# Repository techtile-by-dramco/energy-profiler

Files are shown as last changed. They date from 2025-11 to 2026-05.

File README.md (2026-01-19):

# 🔍 Energy Profiler 🔍

This repository contains 
- the **hardware** files (including the controller board)
- the **firmware** running on the controller board
- the **publisher script** (which receives information from the controller board over a USB connection)
- an example **subscriber script**

### Updates ToDo 📝
- ???

### Test Energy Profiler script
1. Test `/publisher-script/main_last.py`
2. Run services
	1. Copy service files to systemd:
	```
	sudo cp ~/energy-profiler/ep.service /lib/systemd/system/
 	```
 	2. Enable and start services
  	```
   	sudo systemctl enable ep.service
   	sudo systemctl start ep.service
  	```   
### Update energy profiler service
	
```
sudo cp ~/energy-profiler/ep.service /etc/systemd/system/
sudo systemctl daemon-reload
sudo systemctl restart ep.service
```

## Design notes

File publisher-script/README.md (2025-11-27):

### Publischer script

Executed on the windows server

NRF52 development board is used to receive BLE advertisement packets and communicates/send them to the windows computer via a serial port.

Finally the energy profiler data from serial port is published via ZMQ on port 5556

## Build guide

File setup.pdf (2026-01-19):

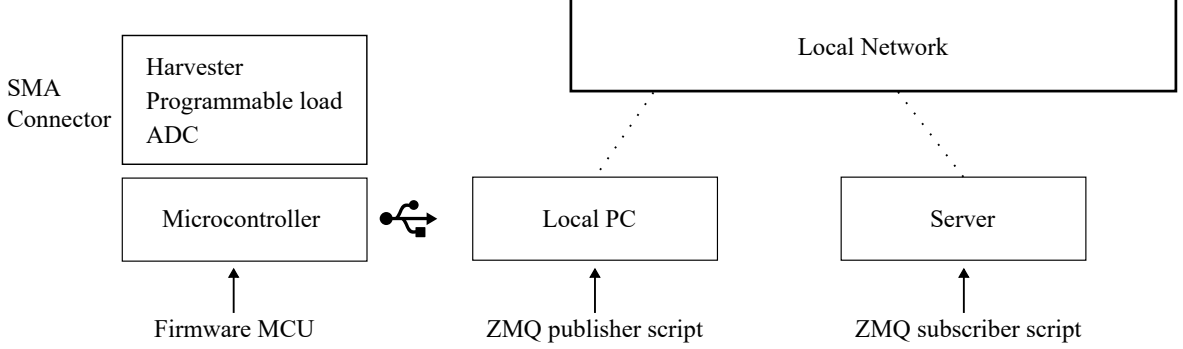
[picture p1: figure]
Microcontroller; Firmware MCU; Local PC; Local Network; Server; Programmable load; Harvester; ADC; SMA Connector; ZMQ publisher script; ZMQ subscriber script

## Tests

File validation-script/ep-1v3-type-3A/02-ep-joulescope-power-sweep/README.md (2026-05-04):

## JouleScope Measuements

Votage of the power supply was 2V in following measurement.
Power supply was connected to the joulescope and the energy profiler.
The current passes through the JouleScope.

"Joulescope switches shunt resistors in approximately 1 μs on over-range to keep your target device running correctly. It maintains a maximum burden voltage of 20 mV across the shunt resistor, for any current up to 2 A. Joulescope is electrically isolated to avoid any grounding and ground loop concerns." [See here](https://www.joulescope.com/blogs/blog/how-to-measure-current).

### Processing 1: Results

Power consumed in the EP calculated via energy profiler itself.

<!-- ![](https://github.com/techtile-by-dramco/energy-profiler/blob/main/validation-script/ep-1v3/02-ep-joulescope-power-sweep/js_vs_ep_P1.png)
![](https://github.com/techtile-by-dramco/energy-profiler/blob/main/validation-script/ep-1v3/02-ep-joulescope-power-sweep/js_vs_ep_delta_P1.png)
![](https://github.com/techtile-by-dramco/energy-profiler/blob/main/validation-script/ep-1v3/02-ep-joulescope-power-sweep/js_vs_ep_error_P1.png)
![](https://github.com/techtile-by-dramco/energy-profiler/blob/main/validation-script/ep-1v3/02-ep-joulescope-power-sweep/js_vs_ep_error_log_P1.png)
![](https://github.com/techtile-by-dramco/energy-profiler/blob/main/validation-script/ep-1v3/02-ep-joulescope-power-sweep/js_vs_pot_val_P1.png) -->

### Processing 2: Results

Power consumed in the EP NOT calculated via energy profiler itself.

Due to energy loss over the internal JouleScope shunt resistor, the voltage measured by the energy profiler drops.
Therefore the EP power is calculated via JouleScope voltage in the following graphs.

<!-- ![](https://github.com/techtile-by-dramco/energy-profiler/blob/main/validation-script/ep-1v3/02-ep-joulescope-power-sweep/js_vs_ep_P2.png)
![](https://github.com/techtile-by-dramco/energy-profiler/blob/main/validation-script/ep-1v3/02-ep-joulescope-power-sweep/js_vs_ep_delta_P2.png)
![](https://github.com/techtile-by-dramco/energy-profiler/blob/main/validation-script/ep-1v3/02-ep-joulescope-power-sweep/js_vs_ep_error_P2.png)
![](https://github.com/techtile-by-dramco/energy-profiler/blob/main/validation-script/ep-1v3/02-ep-joulescope-power-sweep/js_vs_ep_error_log_P2.png)
![](https://github.com/techtile-by-dramco/energy-profiler/blob/main/validation-script/ep-1v3/02-ep-joulescope-power-sweep/js_vs_pot_val_P2.png) -->

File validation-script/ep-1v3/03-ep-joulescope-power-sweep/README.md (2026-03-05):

## JouleScope Measuements

Voltage with the JouleScope is measured after the JouleScope shunt resistor

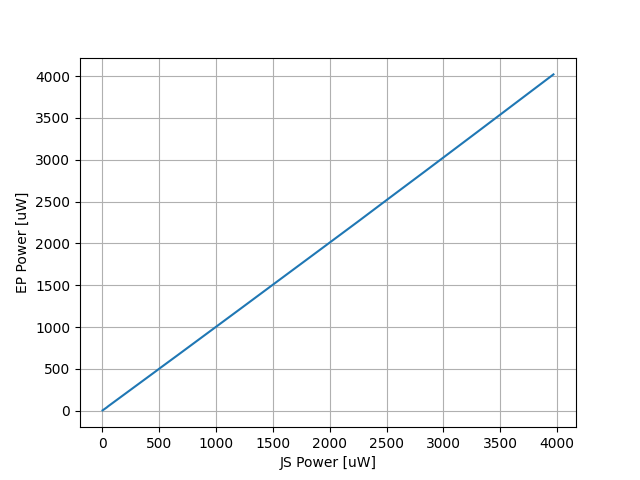
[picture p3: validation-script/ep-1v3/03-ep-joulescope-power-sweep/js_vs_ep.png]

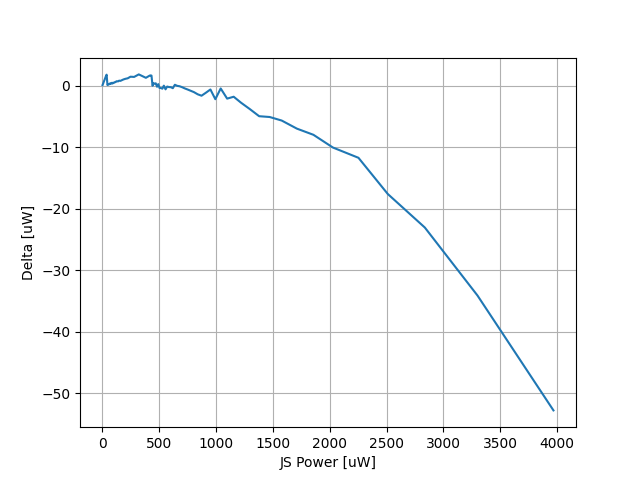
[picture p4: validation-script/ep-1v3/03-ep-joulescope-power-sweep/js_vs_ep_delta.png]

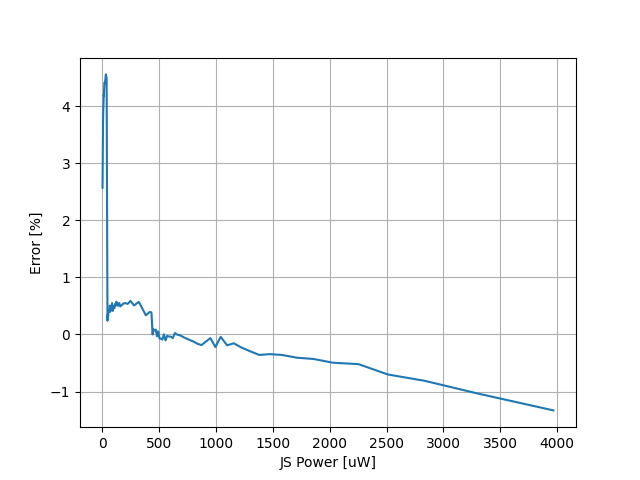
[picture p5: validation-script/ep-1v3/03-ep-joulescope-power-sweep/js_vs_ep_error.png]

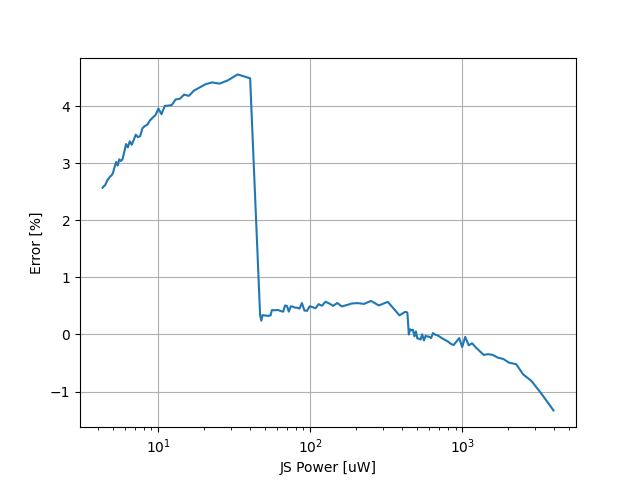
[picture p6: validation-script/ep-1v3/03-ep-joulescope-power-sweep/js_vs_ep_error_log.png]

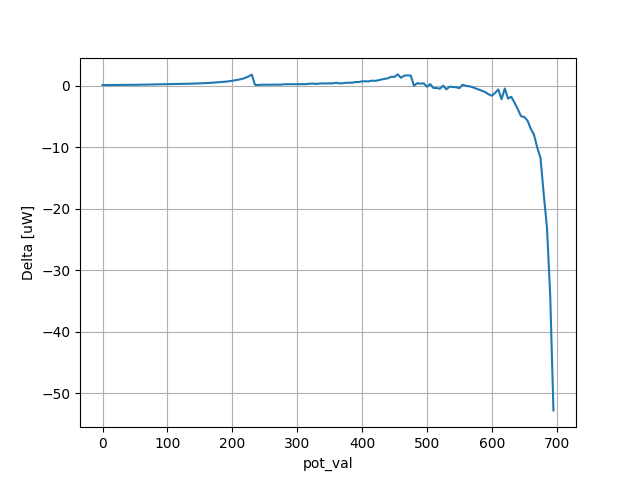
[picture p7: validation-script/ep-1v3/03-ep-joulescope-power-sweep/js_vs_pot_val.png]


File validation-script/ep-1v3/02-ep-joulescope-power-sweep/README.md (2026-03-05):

## JouleScope Measuements

Votage of the power supply was 2V in following measurement.
Power supply was connected to the joulescope and the energy profiler.
The current passes through the JouleScope.

"Joulescope switches shunt resistors in approximately 1 μs on over-range to keep your target device running correctly. It maintains a maximum burden voltage of 20 mV across the shunt resistor, for any current up to 2 A. Joulescope is electrically isolated to avoid any grounding and ground loop concerns." [See here](https://www.joulescope.com/blogs/blog/how-to-measure-current).

### Processing 1: Results

Power consumed in the EP calculated via energy profiler itself.

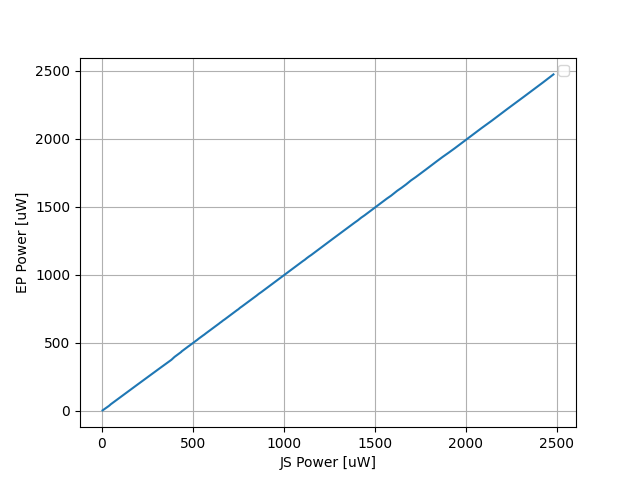
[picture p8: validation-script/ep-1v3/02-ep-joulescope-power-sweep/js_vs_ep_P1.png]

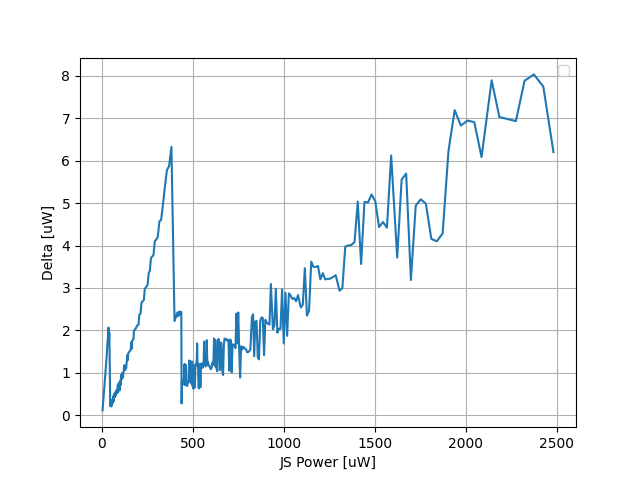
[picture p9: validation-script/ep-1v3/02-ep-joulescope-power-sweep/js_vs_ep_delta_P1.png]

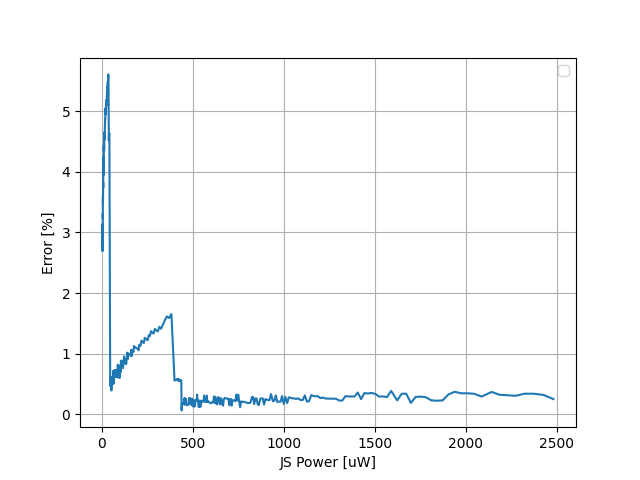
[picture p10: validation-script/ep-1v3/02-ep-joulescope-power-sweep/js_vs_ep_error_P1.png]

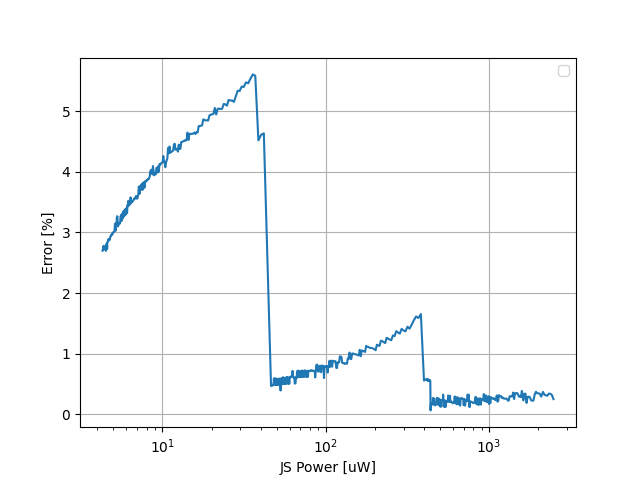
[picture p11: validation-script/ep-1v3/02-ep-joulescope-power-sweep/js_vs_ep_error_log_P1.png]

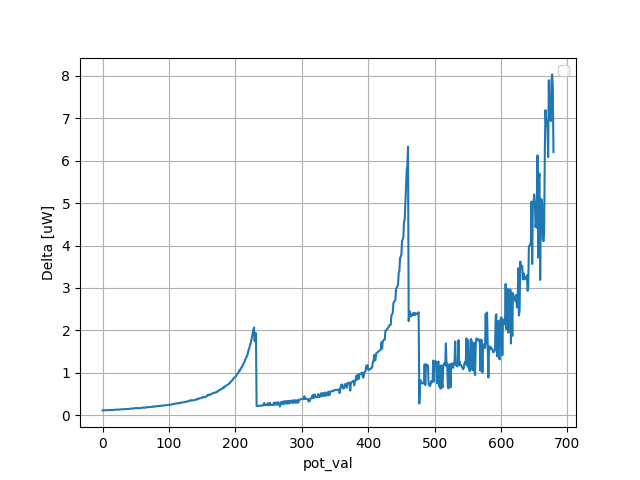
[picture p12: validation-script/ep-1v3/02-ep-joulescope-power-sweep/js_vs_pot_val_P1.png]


### Processing 2: Results

Power consumed in the EP NOT calculated via energy profiler itself.

Due to energy loss over the internal JouleScope shunt resistor, the voltage measured by the energy profiler drops.
Therefore the EP power is calculated via JouleScope voltage in the following graphs.







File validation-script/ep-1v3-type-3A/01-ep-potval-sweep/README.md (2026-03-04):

## Potentiometer calibration

The HAMEG HM8112-3 was connected to the input of the energy profiler. The AUTO_RESISTANCE_TUNE parameter was disabled in the firmware. A sweep was performed over all potentiometer values to calibrate the energy profiler using a lookup table implemented in the firmware. The results of the calibrated energy profiler are presented below.



### Sweep


### Error (absolute)


### Error (percentage)


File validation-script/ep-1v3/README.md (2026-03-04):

## Validation with Measuements of Energy Profiler Version 1.3

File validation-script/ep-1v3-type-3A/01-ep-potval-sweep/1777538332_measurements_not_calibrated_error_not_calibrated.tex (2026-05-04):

% This file was created with matplot2tikz v0.5.4.
\begin{tikzpicture}

\definecolor{darkgray176}{RGB}{176,176,176}
\definecolor{steelblue31119180}{RGB}{31,119,180}

\begin{axis}[
tick align=outside,
tick pos=left,
x grid style={darkgray176},
xlabel={Digital potentiometer Index},
xmajorgrids,
xmin=-35.9, xmax=753.9,
xtick style={color=black},
y grid style={darkgray176},
ylabel={Resistance Error},
ymajorgrids,
ymin=-8861.3, ymax=40359.3,
ytick style={color=black}
]
\addplot [semithick, steelblue31119180]
table {%
0 38122
1 37749
2 37259
3 36760
4 36537
5 36312
6 35439
7 34929
8 34951
9 34097
10 33705
11 33231
12 32777
13 32348
14 31900
15 30555
16 29917
17 30210
18 29782
19 29692
20 29167
21 29634
22 31906
23 28051
24 27577
25 27153
26 26771
27 26415
28 25956
29 25496
30 25150
31 24737
32 24340
33 24346
34 23442
35 23142
36 22827
37 22362
38 22057
39 21357
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
};
\end{axis}

\end{tikzpicture}

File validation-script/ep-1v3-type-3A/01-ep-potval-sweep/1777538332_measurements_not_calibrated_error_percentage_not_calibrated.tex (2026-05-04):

% This file was created with matplot2tikz v0.5.4.
\begin{tikzpicture}

\definecolor{darkgray176}{RGB}{176,176,176}
\definecolor{steelblue31119180}{RGB}{31,119,180}

\begin{axis}[
tick align=outside,
tick pos=left,
x grid style={darkgray176},
xlabel={Digital potentiometer Index},
xmajorgrids,
xmin=-35.9, xmax=753.9,
xtick style={color=black},
y grid style={darkgray176},
ylabel={Resistance Error [\%]},
ymajorgrids,
ymin=-80.74061, ymax=7.83852428571429,
ytick style={color=black}
]
\addplot [semithick, steelblue31119180]
table {%
0 3.8122
1 3.78970638283775
2 3.75523968767984
3 3.71958987373024
4 3.71169523809524
5 3.70353749433944
6 3.62895545802519
7 3.59109489891596
8 3.60784516129032
9 3.53394282800414
10 3.5075140201699
11 3.4723013152134
12 3.43889836065574
13 3.40785783666134
14 3.37454723942994
15 3.2456772104703
16 3.19114666666667
17 3.23588544472806
18 3.20344373966722
19 3.20723799689127
20 3.16387796610169
21 3.22821710560717
22 3.49057284954412
23 3.0819991298195
24 3.04297931034483
25 3.00916613748874
26 2.97973035393689
27 2.95294405671799
28 2.91435789473684
29 2.87532225577918
30 2.84885117103075
31 2.81452168946395
32 2.78171428571429
33 2.79487953639852
34 2.70322318023679
35 2.68070303875563
36 2.65623272727273
37 2.6140077711849
38 2.59018133735418
39 2.51953622695999
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
};
\end{axis}

\end{tikzpicture}

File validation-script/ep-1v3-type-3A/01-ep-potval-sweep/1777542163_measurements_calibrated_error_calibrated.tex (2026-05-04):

% This file was created with matplot2tikz v0.5.4.
\begin{tikzpicture}

\definecolor{darkgray176}{RGB}{176,176,176}
\definecolor{steelblue31119180}{RGB}{31,119,180}

\begin{axis}[
tick align=outside,
tick pos=left,
x grid style={darkgray176},
xlabel={Digital potentiometer Index},
xmajorgrids,
xmin=-35.9, xmax=753.9,
xtick style={color=black},
y grid style={darkgray176},
ylabel={Resistance Error},
ymajorgrids,
ymin=-3602.4, ymax=1378.4,
ytick style={color=black}
]
\addplot [semithick, steelblue31119180]
table {%
0 81
1 0
2 -10
3 5
4 61
5 -107
6 220
7 281
8 -804
9 1071
10 -195
11 -36
12 -507
13 308
14 36
15 963
16 1152
17 266
18 210
19 -102
20 0
21 -435
22 -3376
23 107
24 30
25 36
26 10
27 5
28 41
29 31
30 10
31 16
32 10
33 -363
34 184
35 67
36 -62
37 46
38 179
39 410
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
};
\end{axis}

\end{tikzpicture}

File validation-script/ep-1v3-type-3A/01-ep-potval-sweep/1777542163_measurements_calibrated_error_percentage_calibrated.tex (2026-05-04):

% This file was created with matplot2tikz v0.5.4.
\begin{tikzpicture}

\definecolor{darkgray176}{RGB}{176,176,176}
\definecolor{steelblue31119180}{RGB}{31,119,180}

\begin{axis}[
tick align=outside,
tick pos=left,
x grid style={darkgray176},
xlabel={Digital potentiometer Index},
xmajorgrids,
xmin=-35.9, xmax=753.9,
xtick style={color=black},
y grid style={darkgray176},
ylabel={Resistance Error [\%]},
ymajorgrids,
ymin=-0.408689250675512, ymax=0.163101726902093,
ytick style={color=black}
]
\addplot [semithick, steelblue31119180]
table {%
0 0.00842102636716923
1 0
2 -0.00104719937000486
3 0.000525474477179169
4 0.00643569892745385
5 -0.011332872957435
6 0.0233763280676383
7 0.0299660775470899
8 -0.0860998994430279
9 0.115068987672254
10 -0.0210303354500276
11 -0.00389694739121022
12 -0.0550878580710775
13 0.0335925485619553
14 0.00394126637267739
15 0.105725305236532
16 0.126930539686177
17 0.0294448755400533
18 0.0233357965563032
19 -0.0113827979140465
20 0
21 -0.0489680683166467
22 -0.382698751694712
23 0.0121300752178029
24 0.00341423942695405
25 0.00411339252048127
26 0.00114722841088215
27 0.000575959894760608
28 0.00474169884661067
29 0.00359953647259359
30 0.0011659604832673
31 0.0018731656147671
32 0.00117555780217713
33 -0.0428699481663354
34 0.0218075366372541
35 0.00797487082494682
36 -0.00741140974576474
37 0.00552150626690961
38 0.0215791345440956
39 0.0496188425739351
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
};
\end{axis}

\end{tikzpicture}

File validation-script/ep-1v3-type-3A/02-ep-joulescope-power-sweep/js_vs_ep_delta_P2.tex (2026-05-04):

% This file was created with matplot2tikz v0.5.4.
\begin{tikzpicture}

\definecolor{darkgray176}{RGB}{176,176,176}
\definecolor{lightgray204}{RGB}{204,204,204}
\definecolor{steelblue31119180}{RGB}{31,119,180}

\begin{axis}[
legend style={fill opacity=0.8, draw opacity=1, text opacity=1, draw=lightgray204},
tick align=outside,
tick pos=left,
x grid style={darkgray176},
xlabel={JS Power [uW]},
xmajorgrids,
xmin=-233.2205937, xmax=4991.8739117,
xtick style={color=black},
y grid style={darkgray176},
ylabel={Delta [uW]},
ymajorgrids,
ymin=-70.1543704877304, ymax=4.12483284258161,
ytick style={color=black}
]
\addplot [semithick, steelblue31119180, forget plot]
table {%
4.283702 0.108519700373644
5.257069 0.162079146779064
6.857045 0.235530076043274
9.957532 0.377918956282966
18.574586 0.748505418476522
46.487507 0.088198593324624
57.977337 0.113213541429296
77.637837 0.0621449835422784
119.504621 -0.00899385581643879
269.588484 -1.16025192665005
473.771242 -1.38446079223853
609.882185 -2.40871300274432
857.477777 -5.0686147525773
1447.21254 -14.2197744104803
4754.369616 -66.7780430636253
};
\end{axis}

\end{tikzpicture}

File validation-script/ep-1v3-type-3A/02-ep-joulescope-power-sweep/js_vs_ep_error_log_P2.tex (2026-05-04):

% This file was created with matplot2tikz v0.5.4.
\begin{tikzpicture}

\definecolor{darkgray176}{RGB}{176,176,176}
\definecolor{lightgray204}{RGB}{204,204,204}
\definecolor{steelblue31119180}{RGB}{31,119,180}

\begin{axis}[
legend style={fill opacity=0.8, draw opacity=1, text opacity=1, draw=lightgray204},
log basis x={10},
tick align=outside,
tick pos=left,
x grid style={darkgray176},
xlabel={JS Power [uW]},
xmajorgrids,
xmin=3.01686284612116, xmax=6750.82152275626,
xmode=log,
xtick style={color=black},
y grid style={darkgray176},
ylabel={Error [\%]},
ymajorgrids,
ymin=-1.67627596174634, ymax=4.30144318248175,
ytick style={color=black}
]
\addplot [semithick, steelblue31119180, forget plot]
table {%
4.283702 2.53331581827223
5.257069 3.08307056230504
6.857045 3.43486262731649
9.957532 3.79530747461284
18.574586 4.02972867592592
46.487507 0.189725367128472
57.977337 0.195272061959824
77.637837 0.0800447126602438
119.504621 -0.00752594815261478
269.588484 -0.430378890609455
473.771242 -0.292221365398648
609.882185 -0.394947263912016
857.477777 -0.591107418586465
1447.21254 -0.982562962761521
4754.369616 -1.40456145519052
};
\end{axis}

\end{tikzpicture}

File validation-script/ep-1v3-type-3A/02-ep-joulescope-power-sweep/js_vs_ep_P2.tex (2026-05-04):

% This file was created with matplot2tikz v0.5.4.
\begin{tikzpicture}

\definecolor{darkgray176}{RGB}{176,176,176}
\definecolor{lightgray204}{RGB}{204,204,204}
\definecolor{steelblue31119180}{RGB}{31,119,180}

\begin{axis}[
legend style={fill opacity=0.8, draw opacity=1, text opacity=1, draw=lightgray204},
tick align=outside,
tick pos=left,
x grid style={darkgray176},
xlabel={JS Power [uW]},
xmajorgrids,
xmin=-233.2205937, xmax=4991.8739117,
xtick style={color=black},
y grid style={darkgray176},
ylabel={EP Power [uW]},
ymajorgrids,
ymin=-236.673441538574, ymax=5061.99628290183,
ytick style={color=black}
]
\addplot [semithick, steelblue31119180, forget plot]
table {%
4.283702 4.17518229962636
5.257069 5.09498985322094
6.857045 6.62151492395673
9.957532 9.57961304371703
18.574586 17.8260805815235
46.487507 46.3993084066754
57.977337 57.8641234585707
77.637837 77.5756920164577
119.504621 119.513614855816
269.588484 270.74873592665
473.771242 475.155702792239
609.882185 612.290898002744
857.477777 862.546391752577
1447.21254 1461.43231441048
4754.369616 4821.14765906363
};
\end{axis}

\end{tikzpicture}

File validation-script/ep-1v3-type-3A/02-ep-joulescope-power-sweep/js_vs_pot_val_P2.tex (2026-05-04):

% This file was created with matplot2tikz v0.5.4.
\begin{tikzpicture}

\definecolor{darkgray176}{RGB}{176,176,176}
\definecolor{lightgray204}{RGB}{204,204,204}
\definecolor{steelblue31119180}{RGB}{31,119,180}

\begin{axis}[
legend style={fill opacity=0.8, draw opacity=1, text opacity=1, draw=lightgray204},
tick align=outside,
tick pos=left,
x grid style={darkgray176},
xlabel={pot\_val},
xmajorgrids,
xmin=-35, xmax=735,
xtick style={color=black},
y grid style={darkgray176},
ylabel={Delta [uW]},
ymajorgrids,
ymin=-70.1543704877304, ymax=4.12483284258161,
ytick style={color=black}
]
\addplot [semithick, steelblue31119180, forget plot]
table {%
0 0.108519700373644
50 0.162079146779064
100 0.235530076043274
150 0.377918956282966
200 0.748505418476522
250 0.088198593324624
300 0.113213541429296
350 0.0621449835422784
400 -0.00899385581643879
450 -1.16025192665005
500 -1.38446079223853
550 -2.40871300274432
600 -5.0686147525773
650 -14.2197744104803
700 -66.7780430636253
};
\end{axis}

\end{tikzpicture}

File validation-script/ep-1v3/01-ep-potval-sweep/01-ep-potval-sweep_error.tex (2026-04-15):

% This file was created with matplot2tikz v0.5.4.
\begin{tikzpicture}

\definecolor{darkgray176}{RGB}{176,176,176}
\definecolor{steelblue31119180}{RGB}{31,119,180}

\begin{axis}[
tick align=outside,
tick pos=left,
x grid style={darkgray176},
xlabel={Digital potentiometer Index},
xmajorgrids,
xmin=-35.9, xmax=753.9,
xtick style={color=black},
y grid style={darkgray176},
ylabel={Resistance Error},
ymajorgrids,
ymin=-6961.65, ymax=42860.65,
ytick style={color=black}
]
\addplot [semithick, steelblue31119180]
table {%
0 40596
1 40197
2 39621
3 39029
4 38457
5 38407
6 38154
7 37674
8 37190
9 36838
10 36399
11 35941
12 35436
13 35027
14 34604
15 34120
16 33615
17 33196
18 32784
19 32310
20 31979
21 31417
22 30978
23 30745
24 30297
25 29929
26 29542
27 29211
28 28809
29 28359
30 27921
31 27508
32 27173
33 26861
34 26551
35 26087
36 25659
37 25287
38 24956
39 24651
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
};
\end{axis}

\end{tikzpicture}

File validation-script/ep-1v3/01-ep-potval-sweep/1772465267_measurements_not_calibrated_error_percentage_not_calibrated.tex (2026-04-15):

% This file was created with matplot2tikz v0.5.4.
\begin{tikzpicture}

\definecolor{darkgray176}{RGB}{176,176,176}
\definecolor{steelblue31119180}{RGB}{31,119,180}

\begin{axis}[
tick align=outside,
tick pos=left,
x grid style={darkgray176},
xlabel={Digital potentiometer Index},
xmajorgrids,
xmin=-35.9, xmax=753.9,
xtick style={color=black},
y grid style={darkgray176},
ylabel={Resistance Error [\%]},
ymajorgrids,
ymin=-77.2364055304427, ymax=7.96451613929622,
ytick style={color=black}
]
\addplot [semithick, steelblue31119180]
table {%
0 4.0596
1 4.03546656788071
2 3.99329965016675
3 3.94918044564248
4 3.90674285714286
5 3.91721096455978
6 3.90697160036946
7 3.87331183892353
8 3.83896774193548
9 3.81803049822614
10 3.78786538555597
11 3.75546873612245
12 3.71787540983607
13 3.69009015842515
14 3.66059036593209
15 3.62436610771548
16 3.5856
17 3.55572503221425
18 3.52634811501075
19 3.49002625891004
20 3.46890847457627
21 3.42245045578931
22 3.38904800768438
23 3.37799234416957
24 3.34311724137931
25 3.31680968323575
26 3.28815487340793
27 3.26551008293732
28 3.23469473684211
29 3.19819829979768
30 3.16273453464611
31 3.12980000136533
32 3.10548571428571
33 3.08359727376985
34 3.06173870226376
35 3.02184340904062
36 2.98577454545455
37 2.95592587916789
38 2.93061456476451
39 2.90813726322942
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
};
\end{axis}

\end{tikzpicture}

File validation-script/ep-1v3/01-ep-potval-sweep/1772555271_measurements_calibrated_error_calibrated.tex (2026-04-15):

% This file was created with matplot2tikz v0.5.4.
\begin{tikzpicture}

\definecolor{darkgray176}{RGB}{176,176,176}
\definecolor{steelblue31119180}{RGB}{31,119,180}

\begin{axis}[
tick align=outside,
tick pos=left,
x grid style={darkgray176},
xlabel={Digital potentiometer Index},
xmajorgrids,
xmin=-35.9, xmax=753.9,
xtick style={color=black},
y grid style={darkgray176},
ylabel={Resistance Error},
ymajorgrids,
ymin=-168.1, ymax=164.1,
ytick style={color=black}
]
\addplot [semithick, steelblue31119180]
table {%
0 -30
1 -77
2 97
3 -153
4 41
5 -82
6 -36
7 149
8 -5
9 -10
10 0
11 -46
12 -5
13 -10
14 -87
15 25
16 -46
17 -62
18 31
19 -6
20 15
21 0
22 -87
23 21
24 56
25 46
26 -62
27 -103
28 -72
29 -30
30 -10
31 -41
32 15
33 -5
34 -36
35 16
36 -92
37 -26
38 26
39 20
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
};
\end{axis}

\end{tikzpicture}

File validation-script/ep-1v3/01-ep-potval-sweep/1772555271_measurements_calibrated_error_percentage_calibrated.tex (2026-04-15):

% This file was created with matplot2tikz v0.5.4.
\begin{tikzpicture}

\definecolor{darkgray176}{RGB}{176,176,176}
\definecolor{steelblue31119180}{RGB}{31,119,180}

\begin{axis}[
tick align=outside,
tick pos=left,
x grid style={darkgray176},
xlabel={Digital potentiometer Index},
xmajorgrids,
xmin=-35.9, xmax=753.9,
xtick style={color=black},
y grid style={darkgray176},
ylabel={Resistance Error [\%]},
ymajorgrids,
ymin=-0.988110161223086, ymax=0.0637462215058465,
ytick style={color=black}
]
\addplot [semithick, steelblue31119180]
table {%
0 -0.00312650463035336
1 -0.00805423323176631
2 0.0101817601639158
3 -0.016116205213013
4 0.00433375860541762
5 -0.00870366360552449
6 -0.00383607186241289
7 0.0159345677454405
8 -0.000536663221288786
9 -0.0010774132170589
10 0
11 -0.00499344339172044
12 -0.000544761410844892
13 -0.00109372214426414
14 -0.00955188485038125
15 0.00275505166272878
16 -0.00508847868867692
17 -0.00688503327025754
18 0.00345586415555402
19 -0.000671472920616233
20 0.00168543492086321
21 0
22 -0.00985058809143157
23 0.00238775287439965
24 0.00639228542467605
25 0.00527198273540262
26 -0.00713466214497864
27 -0.0119017080684337
28 -0.0083537536199599
29 -0.00349468691099964
30 -0.00116957833192399
31 -0.00481506056993875
32 0.00176900352031701
33 -0.000592182714423439
34 -0.00428176894147536
35 0.00191085388894595
36 -0.0110333711506127
37 -0.00313142091837349
38 0.00314496219392563
39 0.00242983251164497
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
};
\end{axis}

\end{tikzpicture}

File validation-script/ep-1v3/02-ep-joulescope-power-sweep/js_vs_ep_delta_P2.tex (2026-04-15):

% This file was created with matplot2tikz v0.5.4.
\begin{tikzpicture}

\definecolor{darkgray176}{RGB}{176,176,176}
\definecolor{lightgray204}{RGB}{204,204,204}
\definecolor{steelblue31119180}{RGB}{31,119,180}

\begin{axis}[
legend style={fill opacity=0.8, draw opacity=1, text opacity=1, draw=lightgray204},
tick align=outside,
tick pos=left,
x grid style={darkgray176},
xlabel={JS Power [uW]},
xmajorgrids,
xmin=-119.5208606, xmax=2604.4754826,
xtick style={color=black},
y grid style={darkgray176},
ylabel={Delta [uW]},
ymajorgrids,
ymin=-40.7659676658236, ymax=3.71938274758785,
ytick style={color=black}
]
\addplot [semithick, steelblue31119180, forget plot]
table {%
4.297155 0.0908796883395966
4.312918 0.091159855025894
4.329124 0.0925870160682872
4.345608 0.0942152122651693
4.361965 0.0957696912408397
4.377907 0.0939202550428174
4.394714 0.0939649004113125
4.411348 0.0950254415714694
4.428171 0.0961385383150708
4.444979 0.0964519854797022
4.462251 0.0973157805679925
4.479399 0.0981072613264322
4.496801 0.0993986403114731
4.514193 0.0998418342562523
4.531832 0.100546832320504
4.549758 0.101913332016786
4.566749 0.102072444723082
4.58495 0.102925489281557
4.603235 0.103832530060444
4.621894 0.105028838477189
4.640417 0.105382426111656
4.658861 0.106876257188743
4.677908 0.108049214407674
4.696959 0.107833281400087
4.716009 0.108905116230013
4.733925 0.1082403585464
4.754756 0.110227883102013
4.774547 0.110832650237688
4.794985 0.112148018860919
4.81533 0.113716852521882
4.834644 0.114131116509885
4.85518 0.11518622434659
4.876117 0.116222668476947
4.896784 0.116589195574263
4.917412 0.116976924700336
4.938328 0.118102328155715
4.959944 0.119554905767814
4.98117 0.120143664750077
5.003132 0.121085016684025
5.02501 0.121509583283724
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
};
\end{axis}

\end{tikzpicture}

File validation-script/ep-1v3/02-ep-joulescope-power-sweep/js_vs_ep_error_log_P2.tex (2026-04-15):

% This file was created with matplot2tikz v0.5.4.
\begin{tikzpicture}

\definecolor{darkgray176}{RGB}{176,176,176}
\definecolor{lightgray204}{RGB}{204,204,204}
\definecolor{steelblue31119180}{RGB}{31,119,180}

\begin{axis}[
legend style={fill opacity=0.8, draw opacity=1, text opacity=1, draw=lightgray204},
log basis x={10},
tick align=outside,
tick pos=left,
x grid style={darkgray176},
xlabel={JS Power [uW]},
xmajorgrids,
xmin=3.1268837107561, xmax=3409.0713386424,
xmode=log,
xtick style={color=black},
y grid style={darkgray176},
ylabel={Error [\%]},
ymajorgrids,
ymin=-1.84309334241831, ymax=4.34447513496093,
ytick style={color=black}
]
\addplot [semithick, steelblue31119180, forget plot]
table {%
4.297155 2.11488038806132
4.312918 2.11364684016469
4.329124 2.1387009489284
4.345608 2.16805593751598
4.361965 2.1955630373201
4.377907 2.14532321136144
4.394714 2.13813459559171
4.411348 2.15411347215113
4.428171 2.17106652645236
4.444979 2.16990868752591
4.462251 2.18086747177585
4.479399 2.19018804367354
4.496801 2.21043004374605
4.514193 2.21173162636715
4.531832 2.21867960508033
4.549758 2.23997258792194
4.566749 2.23512272566506
4.58495 2.24485521721191
4.603235 2.25564260917472
4.621894 2.27241988840914
4.640417 2.27096888300461
4.658861 2.29404262519837
4.677908 2.30977638738671
4.696959 2.29581057446078
4.716009 2.3092643849919
4.733925 2.28648232801321
4.754756 2.31826581851966
4.774547 2.32132284461097
4.794985 2.33886068175228
4.81533 2.36155886557894
4.834644 2.36069329013438
4.85518 2.37243983429225
4.876117 2.38350860893918
4.896784 2.38093400840762
4.917412 2.37883107415721
4.938328 2.39154483371123
4.959944 2.41040837896182
4.98117 2.41195672402421
5.003132 2.42018433021604
5.02501 2.41809634774307
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
};
\end{axis}

\end{tikzpicture}

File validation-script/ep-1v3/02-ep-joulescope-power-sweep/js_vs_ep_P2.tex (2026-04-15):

% This file was created with matplot2tikz v0.5.4.
\begin{tikzpicture}

\definecolor{darkgray176}{RGB}{176,176,176}
\definecolor{lightgray204}{RGB}{204,204,204}
\definecolor{steelblue31119180}{RGB}{31,119,180}

\begin{axis}[
legend style={fill opacity=0.8, draw opacity=1, text opacity=1, draw=lightgray204},
tick align=outside,
tick pos=left,
x grid style={darkgray176},
xlabel={JS Power [uW]},
xmajorgrids,
xmin=-119.5208606, xmax=2604.4754826,
xtick style={color=black},
y grid style={darkgray176},
ylabel={EP Power [uW]},
ymajorgrids,
ymin=-121.553479586926, ymax=2645.16112818198,
ytick style={color=black}
]
\addplot [semithick, steelblue31119180, forget plot]
table {%
4.297155 4.2062753116604
4.312918 4.22175814497411
4.329124 4.23653698393171
4.345608 4.25139278773483
4.361965 4.26619530875916
4.377907 4.28398674495718
4.394714 4.30074909958869
4.411348 4.31632255842853
4.428171 4.33203246168493
4.444979 4.3485270145203
4.462251 4.36493521943201
4.479399 4.38129173867357
4.496801 4.39740235968853
4.514193 4.41435116574375
4.531832 4.4312851676795
4.549758 4.44784466798321
4.566749 4.46467655527692
4.58495 4.48202451071844
4.603235 4.49940246993956
4.621894 4.51686516152281
4.640417 4.53503457388834
4.658861 4.55198474281126
4.677908 4.56985878559233
4.696959 4.58912571859991
4.716009 4.60710388376999
4.733925 4.6256846414536
4.754756 4.64452811689799
4.774547 4.66371434976231
4.794985 4.68283698113908
4.81533 4.70161314747812
4.834644 4.72051288349012
4.85518 4.73999377565341
4.876117 4.75989433152305
4.896784 4.78019480442574
4.917412 4.80043507529966
4.938328 4.82022567184428
4.959944 4.84038909423219
4.98117 4.86102633524992
5.003132 4.88204698331598
5.02501 4.90350041671628
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
};
\end{axis}

\end{tikzpicture}

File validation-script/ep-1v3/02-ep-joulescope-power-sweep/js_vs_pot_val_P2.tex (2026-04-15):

% This file was created with matplot2tikz v0.5.4.
\begin{tikzpicture}

\definecolor{darkgray176}{RGB}{176,176,176}
\definecolor{lightgray204}{RGB}{204,204,204}
\definecolor{steelblue31119180}{RGB}{31,119,180}

\begin{axis}[
legend style={fill opacity=0.8, draw opacity=1, text opacity=1, draw=lightgray204},
tick align=outside,
tick pos=left,
x grid style={darkgray176},
xlabel={pot\_val},
xmajorgrids,
xmin=-33.95, xmax=712.95,
xtick style={color=black},
y grid style={darkgray176},
ylabel={Delta [uW]},
ymajorgrids,
ymin=-40.7659676658236, ymax=3.71938274758785,
ytick style={color=black}
]
\addplot [semithick, steelblue31119180, forget plot]
table {%
0 0.0908796883395966
1 0.091159855025894
2 0.0925870160682872
3 0.0942152122651693
4 0.0957696912408397
5 0.0939202550428174
6 0.0939649004113125
7 0.0950254415714694
8 0.0961385383150708
9 0.0964519854797022
10 0.0973157805679925
11 0.0981072613264322
12 0.0993986403114731
13 0.0998418342562523
14 0.100546832320504
15 0.101913332016786
16 0.102072444723082
17 0.102925489281557
18 0.103832530060444
19 0.105028838477189
20 0.105382426111656
21 0.106876257188743
22 0.108049214407674
23 0.107833281400087
24 0.108905116230013
25 0.1082403585464
26 0.110227883102013
27 0.110832650237688
28 0.112148018860919
29 0.113716852521882
30 0.114131116509885
31 0.11518622434659
32 0.116222668476947
33 0.116589195574263
34 0.116976924700336
35 0.118102328155715
36 0.119554905767814
37 0.120143664750077
38 0.121085016684025
39 0.121509583283724
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
};
\end{axis}

\end{tikzpicture}

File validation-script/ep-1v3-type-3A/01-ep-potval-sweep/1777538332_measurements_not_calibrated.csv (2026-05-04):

index | epc | measured
0 | 1000000 | 961878.0
1 | 996093 | 958344.0
2 | 992187 | 954928.0
3 | 988281 | 951521.0
4 | 984375 | 947838.0
5 | 980468 | 944156.0
6 | 976562 | 941123.0
7 | 972656 | 937727.0
8 | 968750 | 933799.0
9 | 964843 | 930746.0
10 | 960937 | 927232.0
11 | 957031 | 923800.0
12 | 953125 | 920348.0
13 | 949218 | 916870.0
14 | 945312 | 913412.0
15 | 941406 | 910851.0
16 | 937500 | 907583.0
17 | 933593 | 903383.0
18 | 929687 | 899905.0
19 | 925781 | 896089.0
20 | 921875 | 892708.0
21 | 917968 | 888334.0
22 | 914062 | 882156.0
23 | 910156 | 882105.0
24 | 906250 | 878673.0
25 | 902343 | 875190.0
26 | 898437 | 871666.0
27 | 894531 | 868116.0
28 | 890625 | 864669.0
29 | 886718 | 861222.0
30 | 882812 | 857662.0
31 | 878906 | 854169.0
32 | 875000 | 850660.0
33 | 871093 | 846747.0
34 | 867187 | 843745.0
35 | 863281 | 840139.0
36 | 859375 | 836548.0
37 | 855468 | 833106.0
38 | 851562 | 829505.0
39 | 847656 | 826299.0
40 | 843750 | 820798.0
41 | 839843 | 818672.0
42 | 835937 | 815363.0
43 | 832031 | 811854.0
44 | 828125 | 808248.0
45 | 824218 | 804693.0
46 | 820312 | 801307.0
47 | 816406 | 797973.0
48 | 812500 | 794382.0
49 | 808593 | 792190.0
50 | 804687 | 787442.0
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

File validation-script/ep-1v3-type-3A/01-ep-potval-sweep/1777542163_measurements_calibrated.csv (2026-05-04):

index | epc | measured
0 | 961878 | 961797.0
1 | 958344 | 958344.0
2 | 954928 | 954938.0
3 | 951521 | 951516.0
4 | 947838 | 947777.0
5 | 944156 | 944263.0
6 | 941123 | 940903.0
7 | 937727 | 937446.0
8 | 933799 | 934603.0
9 | 930746 | 929675.0
10 | 927232 | 927427.0
11 | 923800 | 923836.0
12 | 920348 | 920855.0
13 | 916870 | 916562.0
14 | 913412 | 913376.0
15 | 910851 | 909888.0
16 | 907583 | 906431.0
17 | 903383 | 903117.0
18 | 899905 | 899695.0
19 | 896089 | 896191.0
20 | 892708 | 892708.0
21 | 888334 | 888769.0
22 | 882156 | 885532.0
23 | 882105 | 881998.0
24 | 878673 | 878643.0
25 | 875190 | 875154.0
26 | 871666 | 871656.0
27 | 868116 | 868111.0
28 | 864669 | 864628.0
29 | 861222 | 861191.0
30 | 857662 | 857652.0
31 | 854169 | 854153.0
32 | 850660 | 850650.0
33 | 846747 | 847110.0
34 | 843745 | 843561.0
35 | 840139 | 840072.0
36 | 836548 | 836610.0
37 | 833106 | 833060.0
38 | 829505 | 829326.0
39 | 826299 | 825889.0
40 | 820798 | 822355.0
41 | 818672 | 818902.0
42 | 815363 | 815194.0
43 | 811854 | 812023.0
44 | 808248 | 808243.0
45 | 804693 | 804698.0
46 | 801307 | 801292.0
47 | 797973 | 797942.0
48 | 794382 | 794644.0
49 | 792190 | 791253.0
50 | 787442 | 787718.0
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

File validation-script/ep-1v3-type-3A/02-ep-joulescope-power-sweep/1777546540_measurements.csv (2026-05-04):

js_current_pA | js_voltage_mv | js_power_pw | timestamp | buffer_voltage_mv | resistance | pwr_pw | pot_val
2138109 | 2004 | 4283702 | 1777546543649 | 2000 | 961878 | 4158531 | 0
2623997 | 2003 | 5257069 | 1777546547050 | 2000 | 787442 | 5079739 | 50
3422577 | 2003 | 6857045 | 1777546550450 | 1998 | 605905 | 6588498 | 100
4970103 | 2003 | 9957532 | 1777546553850 | 1997 | 418807 | 9522307 | 150
9271093 | 2003 | 18574586 | 1777546557250 | 1992 | 225064 | 17630825 | 200
23203318 | 2003 | 46487507 | 1777546560650 | 2000 | 86467 | 46260423 | 250
28938165 | 2003 | 57977337 | 1777546564050 | 1999 | 69335 | 57633244 | 300
38750246 | 2004 | 77637837 | 1777546567450 | 1998 | 51769 | 77111862 | 350
59646177 | 2004 | 119504621 | 1777546570849 | 1995 | 33603 | 118442549 | 400
134558120 | 2004 | 269588484 | 1777546574249 | 1987 | 14833 | 266174678 | 450
236468626 | 2004 | 473771242 | 1777546577650 | 2000 | 8452 | 473260766 | 500
304398999 | 2004 | 609882185 | 1777546581049 | 1999 | 6559 | 609239365 | 550
427986118 | 2004 | 857477777 | 1777546584449 | 1997 | 4656 | 856531142 | 600
722322618 | 2004 | 1447212540 | 1777546587850 | 1993 | 2748 | 1445432678 | 650
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

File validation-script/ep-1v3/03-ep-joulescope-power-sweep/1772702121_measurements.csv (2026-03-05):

js_current_pA | js_voltage_mv | js_power_pw | timestamp | buffer_voltage_mv | resistance | pwr_pw | pot_val
2139204 | 2006 | 4291547 | 1772702124712 | 2003 | 959538 | 4181188 | 0
2179374 | 2006 | 4372012 | 1772702128110 | 2003 | 942132 | 4258436 | 5
2220914 | 2006 | 4455379 | 1772702131511 | 2003 | 924660 | 4338901 | 10
2264303 | 2006 | 4542277 | 1772702134911 | 2003 | 907424 | 4421316 | 15
2309851 | 2006 | 4633644 | 1772702138310 | 2003 | 889978 | 4507986 | 20
2356868 | 2006 | 4727491 | 1772702141710 | 2003 | 872537 | 4598096 | 25
2406043 | 2006 | 4826164 | 1772702145110 | 2003 | 855009 | 4692358 | 30
2457320 | 2006 | 4928923 | 1772702148511 | 2003 | 837322 | 4791476 | 35
2512028 | 2006 | 5038559 | 1772702151911 | 2003 | 819553 | 4895362 | 40
2568232 | 2006 | 5150853 | 1772702155311 | 2002 | 801661 | 4999624 | 45
2628544 | 2006 | 5271752 | 1772702158711 | 2003 | 784763 | 5112382 | 50
2690293 | 2006 | 5395512 | 1772702162110 | 2003 | 766277 | 5235716 | 55
2755550 | 2005 | 5525934 | 1772702165509 | 2002 | 748277 | 5356310 | 60
2825368 | 2005 | 5665898 | 1772702168910 | 2003 | 730303 | 5493622 | 65
2897677 | 2005 | 5810631 | 1772702172310 | 2003 | 712350 | 5632075 | 70
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

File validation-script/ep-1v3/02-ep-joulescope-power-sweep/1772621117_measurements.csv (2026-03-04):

js_current_pA | js_voltage_mv | js_power_pw | timestamp | buffer_voltage_mv | resistance | pwr_pw | pot_val
2139079 | 2009 | 4297155 | 1772621120680 | 2003 | 959538 | 4181188 | 0
2146976 | 2009 | 4312918 | 1772621124081 | 2003 | 956019 | 4196578 | 1
2155035 | 2009 | 4329124 | 1772621127480 | 2003 | 952684 | 4211269 | 2
2163228 | 2009 | 4345608 | 1772621130880 | 2003 | 949355 | 4226036 | 3
2171430 | 2009 | 4361965 | 1772621134280 | 2003 | 946061 | 4240750 | 4
2179385 | 2009 | 4377907 | 1772621137680 | 2003 | 942132 | 4258436 | 5
2187771 | 2009 | 4394714 | 1772621141081 | 2003 | 938460 | 4275098 | 6
2196033 | 2009 | 4411348 | 1772621144481 | 2003 | 935074 | 4290579 | 7
2204382 | 2009 | 4428171 | 1772621147880 | 2003 | 931683 | 4306195 | 8
2212827 | 2009 | 4444979 | 1772621151280 | 2003 | 928149 | 4322591 | 9
2221381 | 2009 | 4462251 | 1772621154681 | 2003 | 924660 | 4338901 | 10
2229885 | 2009 | 4479399 | 1772621158080 | 2003 | 921208 | 4355160 | 11
2238573 | 2009 | 4496801 | 1772621161481 | 2004 | 917833 | 4375541 | 12
2247211 | 2009 | 4514193 | 1772621164881 | 2003 | 914309 | 4388023 | 13
2255965 | 2009 | 4531832 | 1772621168281 | 2003 | 910815 | 4404856 | 14
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

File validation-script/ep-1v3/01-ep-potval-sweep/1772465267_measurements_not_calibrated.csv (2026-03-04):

index | epc | measured
0 | 1000000 | 959404.0
1 | 996093 | 955896.0
2 | 992187 | 952566.0
3 | 988281 | 949252.0
4 | 984375 | 945918.0
5 | 980468 | 942061.0
6 | 976562 | 938408.0
7 | 972656 | 934982.0
8 | 968750 | 931560.0
9 | 964843 | 928005.0
10 | 960937 | 924538.0
11 | 957031 | 921090.0
12 | 953125 | 917689.0
13 | 949218 | 914191.0
14 | 945312 | 910708.0
15 | 941406 | 907286.0
16 | 937500 | 903885.0
17 | 933593 | 900397.0
18 | 929687 | 896903.0
19 | 925781 | 893471.0
20 | 921875 | 889896.0
21 | 917968 | 886551.0
22 | 914062 | 883084.0
23 | 910156 | 879411.0
24 | 906250 | 875953.0
25 | 902343 | 872414.0
26 | 898437 | 868895.0
27 | 894531 | 865320.0
28 | 890625 | 861816.0
29 | 886718 | 858359.0
30 | 882812 | 854891.0
31 | 878906 | 851398.0
32 | 875000 | 847827.0
33 | 871093 | 844232.0
34 | 867187 | 840636.0
35 | 863281 | 837194.0
36 | 859375 | 833716.0
37 | 855468 | 830181.0
38 | 851562 | 826606.0
39 | 847656 | 823005.0
40 | 843750 | 819404.0
41 | 839843 | 815972.0
42 | 835937 | 812464.0
43 | 832031 | 808909.0
44 | 828125 | 805236.0
45 | 824218 | 801574.0
46 | 820312 | 798173.0
47 | 816406 | 794833.0
48 | 812500 | 791534.0
49 | 808593 | 788138.0
50 | 804687 | 784712.0
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

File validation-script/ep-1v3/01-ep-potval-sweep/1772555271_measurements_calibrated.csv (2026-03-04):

index | epc | measured
0 | 959538 | 959568.0
1 | 956019 | 956096.0
2 | 952684 | 952587.0
3 | 949355 | 949508.0
4 | 946061 | 946020.0
5 | 942132 | 942214.0
6 | 938460 | 938496.0
7 | 935074 | 934925.0
8 | 931683 | 931688.0
9 | 928149 | 928159.0
10 | 924660 | 924660.0
11 | 921208 | 921254.0
12 | 917833 | 917838.0
13 | 914309 | 914319.0
14 | 910815 | 910902.0
15 | 907424 | 907399.0
16 | 904003 | 904049.0
17 | 900504 | 900566.0
18 | 897026 | 896995.0
19 | 893558 | 893564.0
20 | 889978 | 889963.0
21 | 886664 | 886664.0
22 | 883196 | 883283.0
23 | 879488 | 879467.0
24 | 876056 | 876000.0
25 | 872537 | 872491.0
26 | 868997 | 869059.0
27 | 865422 | 865525.0
28 | 861888 | 861960.0
29 | 858446 | 858476.0
30 | 855009 | 855019.0
31 | 851495 | 851536.0
32 | 847935 | 847920.0
33 | 844334 | 844339.0
34 | 840774 | 840810.0
35 | 837322 | 837306.0
36 | 833834 | 833926.0
37 | 830294 | 830320.0
38 | 826719 | 826693.0
39 | 823102 | 823082.0
40 | 819553 | 819609.0
41 | 816044 | 816075.0
42 | 812566 | 812561.0
43 | 809022 | 808929.0
44 | 805328 | 805349.0
45 | 801661 | 801692.0
46 | 798229 | 798301.0
47 | 794900 | 794951.0
48 | 791611 | 791534.0
49 | 788205 | 788261.0
50 | 784763 | 784829.0
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

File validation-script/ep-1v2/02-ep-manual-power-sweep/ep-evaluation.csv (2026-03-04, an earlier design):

resistance | selected_otii_voltage_v | otii_current_ua | measured_ep_power_pw
218100 | 2.5 | 2.95 | 5556871
218100 | 3.0 | 5.05 | 9456500
218100 | 3.5 | 7.3 | 13485573
46420 | 2.0 | 5.29 | 9150501
46420 | 2.5 | 14.1 | 25242459
46420 | 3.0 | 24.7 | 45940218
46420 | 3.5 | 35.5 | 65795919

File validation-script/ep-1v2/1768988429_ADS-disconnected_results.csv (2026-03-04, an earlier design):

index | epc | measured
0 | 1000000.0 | 1005277.0
1 | 996093.75 | 1001355.0
2 | 992187.5 | 997427.0
3 | 988281.25 | 993515.0
4 | 984375.0 | 989591.0
5 | 980468.75 | 985672.0
6 | 976562.5 | 981758.0
7 | 972656.25 | 977840.0
8 | 968750.0 | 973914.0
9 | 964843.75 | 969982.0
10 | 960937.5 | 966072.0
11 | 957031.25 | 962156.0
12 | 953125.0 | 958224.0
13 | 949218.75 | 954302.0
14 | 945312.5 | 950373.0
15 | 941406.25 | 946446.0
16 | 937500.0 | 942666.0
17 | 933593.75 | 938745.0
18 | 929687.5 | 934821.0
19 | 925781.25 | 930901.0
20 | 921875.0 | 926991.0
21 | 917968.75 | 923072.0
22 | 914062.5 | 919152.0
23 | 910156.25 | 915198.0
24 | 906250.0 | 911315.0
25 | 902343.75 | 907382.0
26 | 898437.5 | 903466.0
27 | 894531.25 | 899578.0
28 | 890625.0 | 895589.0
29 | 886718.75 | 891689.0
30 | 882812.5 | 887756.0
31 | 878906.25 | 883845.0
32 | 875000.0 | 879916.0
33 | 871093.75 | 875996.0
34 | 867187.5 | 872071.0
35 | 863281.25 | 868154.0
36 | 859375.0 | 864240.0
37 | 855468.75 | 860313.0
38 | 851562.5 | 856396.0
39 | 847656.25 | 852478.0
40 | 843750.0 | 848561.0
41 | 839843.75 | 844643.0
42 | 835937.5 | 840714.0
43 | 832031.25 | 836791.0
44 | 828125.0 | 832875.0
45 | 824218.75 | 828944.0
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

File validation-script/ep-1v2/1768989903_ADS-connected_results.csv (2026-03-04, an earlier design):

index | epc | measured
0 | 1000000.0 | 1005167.0
1 | 996093.75 | 1001232.0
2 | 992187.5 | 997258.0
3 | 988281.25 | 993423.0
4 | 984375.0 | 989478.0
5 | 980468.75 | 985556.0
6 | 976562.5 | 981625.0
7 | 972656.25 | 977715.0
8 | 968750.0 | 973797.0
9 | 964843.75 | 969877.0
10 | 960937.5 | 965966.0
11 | 957031.25 | 962030.0
12 | 953125.0 | 958195.0
13 | 949218.75 | 954229.0
14 | 945312.5 | 950264.0
15 | 941406.25 | 946336.0
16 | 937500.0 | 942549.0
17 | 933593.75 | 938648.0
18 | 929687.5 | 934712.0
19 | 925781.25 | 930788.0
20 | 921875.0 | 926865.0
21 | 917968.75 | 922995.0
22 | 914062.5 | 919048.0
23 | 910156.25 | 915094.0
24 | 906250.0 | 911195.0
25 | 902343.75 | 907273.0
26 | 898437.5 | 903348.0
27 | 894531.25 | 899418.0
28 | 890625.0 | 895521.0
29 | 886718.75 | 891577.0
30 | 882812.5 | 887656.0
31 | 878906.25 | 883719.0
32 | 875000.0 | 879800.0
33 | 871093.75 | 875880.0
34 | 867187.5 | 871964.0
35 | 863281.25 | 868041.0
36 | 859375.0 | 864132.0
37 | 855468.75 | 860202.0
38 | 851562.5 | 856288.0
39 | 847656.25 | 852371.0
40 | 843750.0 | 848447.0
41 | 839843.75 | 844529.0
42 | 835937.5 | 840560.0
43 | 832031.25 | 836747.0
44 | 828125.0 | 832756.0
45 | 824218.75 | 828928.0
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

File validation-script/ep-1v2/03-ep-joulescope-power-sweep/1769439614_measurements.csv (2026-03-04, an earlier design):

js_current_pA | js_voltage_mv | js_power_pw | timestamp | buffer_voltage_mv | resistance | pwr_pw | pot_val
2110458 | 2009 | 4239286 | 1769439615180 | 2003 | 972083 | 4127228 | 0
2592250 | 2009 | 5207130 | 1769439616379 | 2003 | 794946 | 5046895 | 50
3383193 | 2009 | 6795820 | 1769439617581 | 2002 | 611673 | 6552527 | 100
4919073 | 2009 | 9881222 | 1769439618780 | 2000 | 422264 | 9472746 | 150
9184807 | 2009 | 18449535 | 1769439619980 | 1995 | 226719 | 17554880 | 200
24380189 | 2009 | 48972780 | 1769439621180 | 2003 | 82307 | 48744444 | 250
30319737 | 2009 | 60903616 | 1769439622380 | 2002 | 66222 | 60523753 | 300
40532001 | 2009 | 81414635 | 1769439623580 | 2001 | 49532 | 80836651 | 350
62276312 | 2009 | 125096017 | 1769439624779 | 1998 | 32206 | 123952182 | 400
140448477 | 2009 | 282123404 | 1769439625979 | 1989 | 14213 | 278345247 | 450

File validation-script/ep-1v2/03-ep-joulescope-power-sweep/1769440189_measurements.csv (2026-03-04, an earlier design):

js_current_pA | js_voltage_mv | js_power_pw | timestamp | buffer_voltage_mv | resistance | pwr_pw | pot_val
2110452 | 2009 | 4239275 | 1769440190554 | 2003 | 972083 | 4127228 | 0
2118328 | 2009 | 4255011 | 1769440191953 | 2003 | 968599 | 4142074 | 1
2126209 | 2009 | 4270912 | 1769440193353 | 2003 | 965114 | 4157031 | 2
2134164 | 2009 | 4286924 | 1769440194754 | 2004 | 961627 | 4176272 | 3
2142128 | 2009 | 4302882 | 1769440196153 | 2003 | 958137 | 4187302 | 4
2150113 | 2009 | 4318939 | 1769440197554 | 2004 | 954644 | 4206820 | 5
2158264 | 2009 | 4335315 | 1769440198953 | 2004 | 951150 | 4222274 | 6
2166311 | 2009 | 4351547 | 1769440200354 | 2004 | 947653 | 4237854 | 7
2174680 | 2009 | 4368304 | 1769440201752 | 2003 | 944153 | 4249320 | 8
2182494 | 2009 | 4384017 | 1769440203153 | 2003 | 940650 | 4265145 | 9
2191736 | 2009 | 4402689 | 1769440204552 | 2004 | 937146 | 4285368 | 10
2199777 | 2009 | 4418762 | 1769440205952 | 2004 | 933639 | 4301465 | 11
2207987 | 2009 | 4435176 | 1769440207352 | 2003 | 930129 | 4313389 | 12
2217488 | 2009 | 4454229 | 1769440208752 | 2003 | 926617 | 4329738 | 13
2225261 | 2009 | 4469848 | 1769440210152 | 2003 | 923102 | 4346225 | 14
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

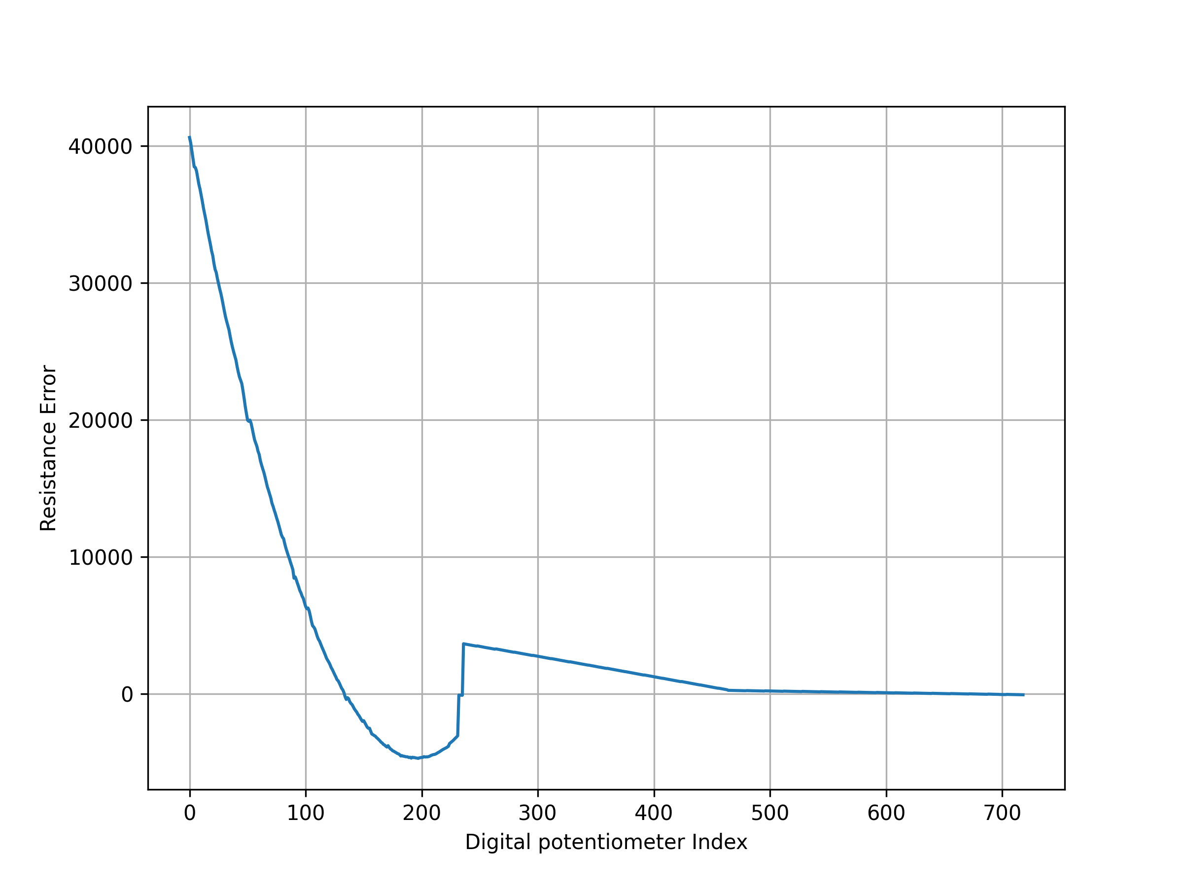
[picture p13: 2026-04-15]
validation-script/ep-1v3/01-ep-potval-sweep/1772465267_measurements_not_calibrated_error.png

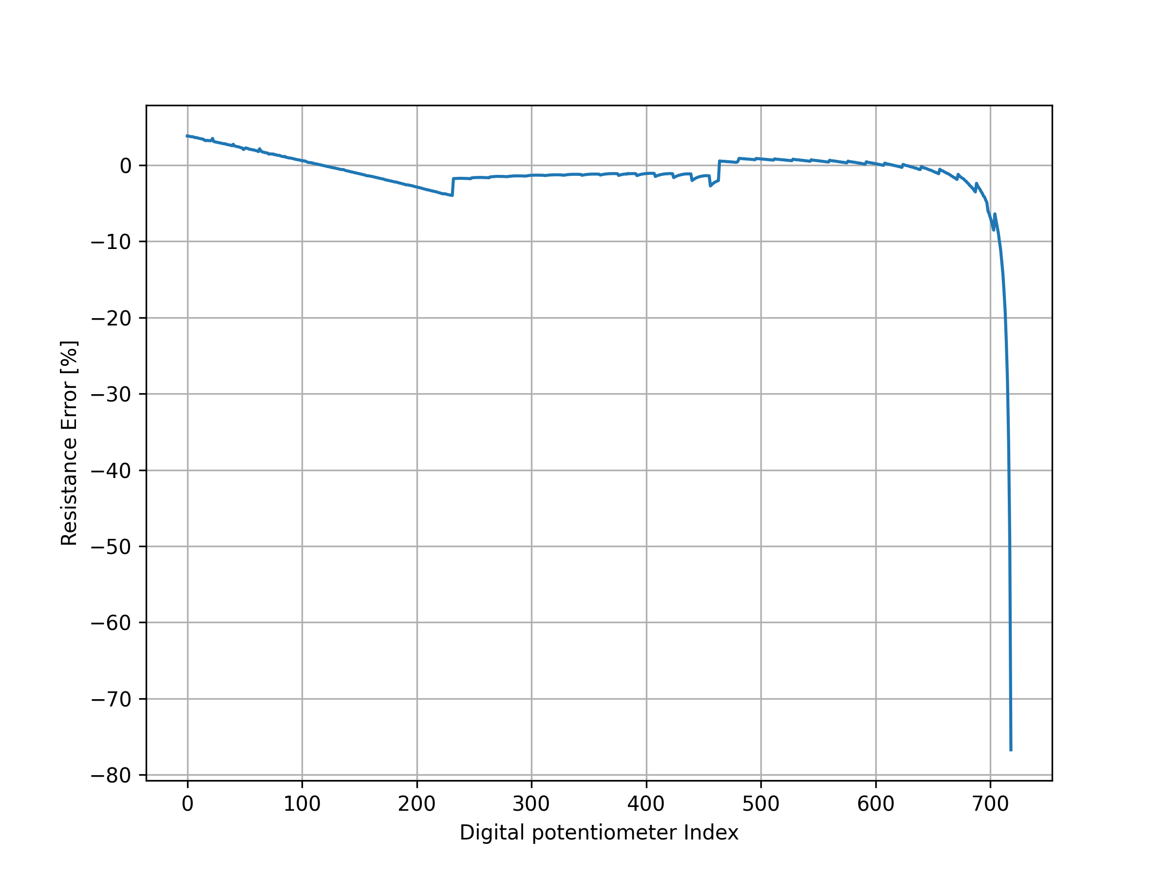
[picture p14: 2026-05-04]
validation-script/ep-1v3-type-3A/01-ep-potval-sweep/1777538332_measurements_not_calibrated_error_percentage.png

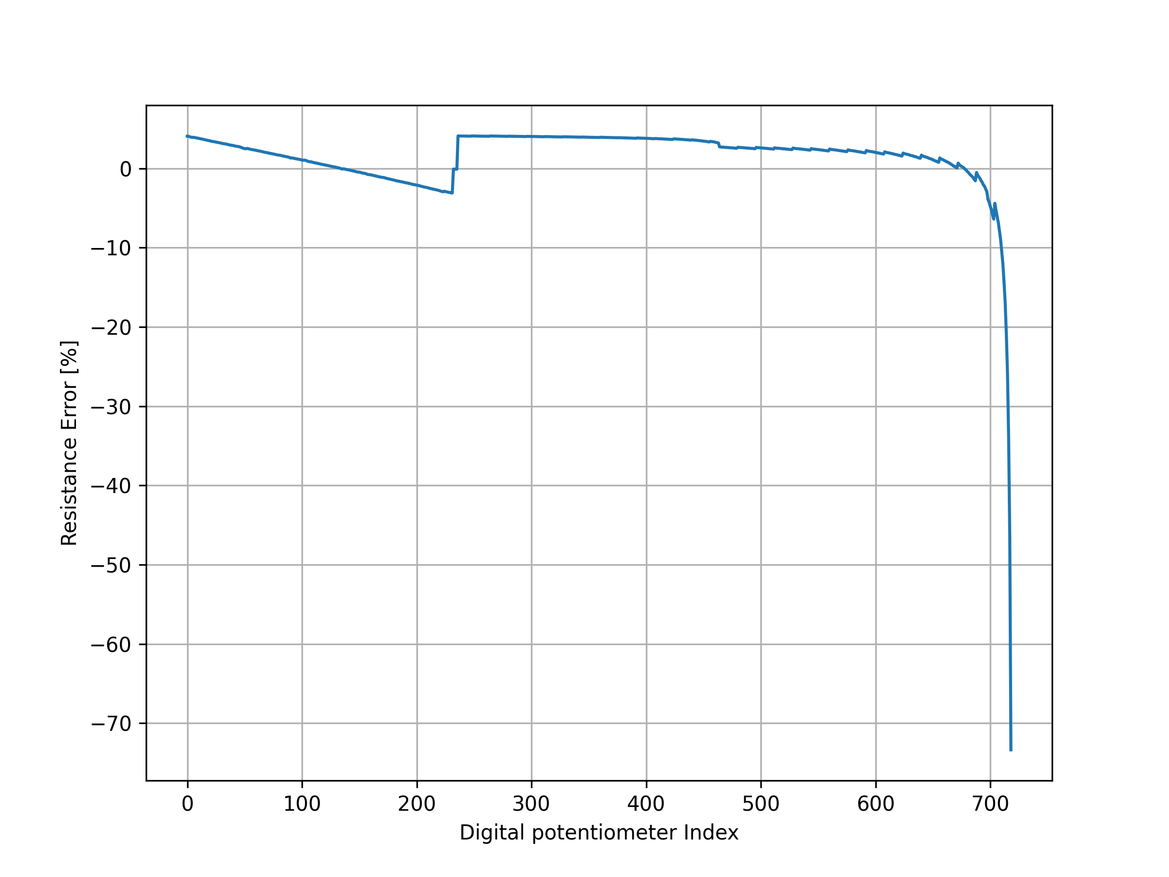
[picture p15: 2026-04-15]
validation-script/ep-1v3/01-ep-potval-sweep/1772465267_measurements_not_calibrated_error_percentage.png

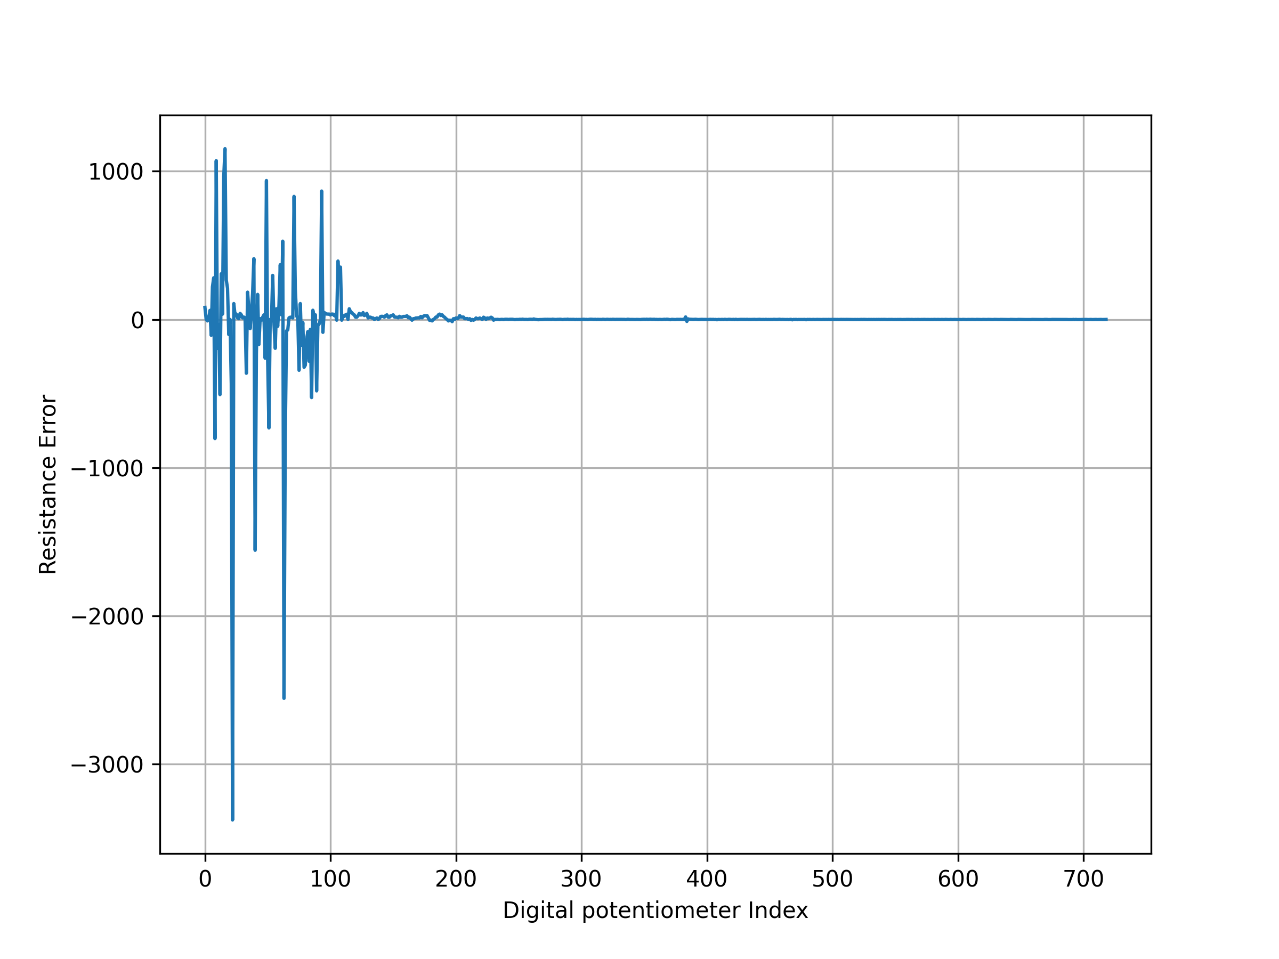
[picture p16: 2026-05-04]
validation-script/ep-1v3-type-3A/01-ep-potval-sweep/1777542163_measurements_calibrated_error.png

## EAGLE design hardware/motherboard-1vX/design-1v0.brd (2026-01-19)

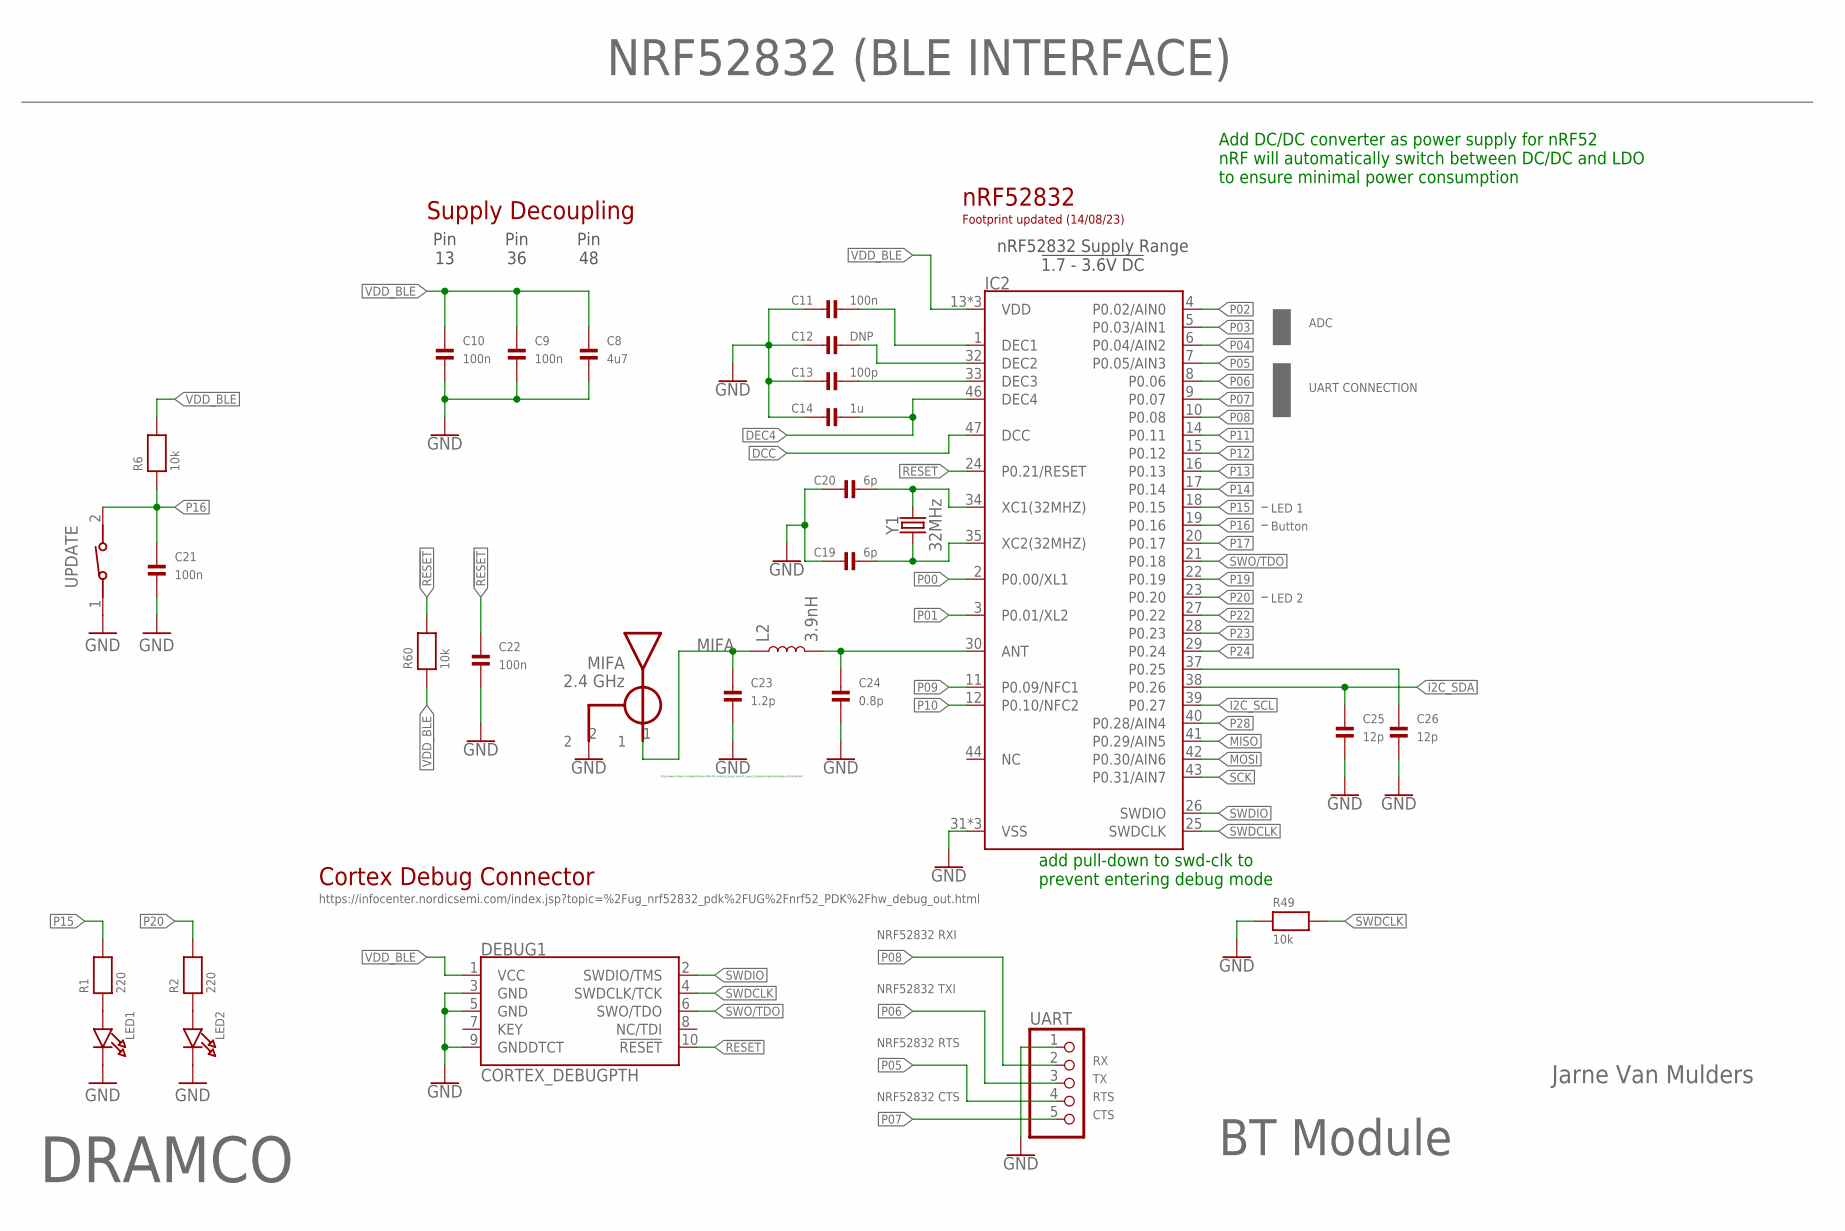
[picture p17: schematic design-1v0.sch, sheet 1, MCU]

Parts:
C8: 4u7; 0603
C9, C10, C11, C21, C22: 100n; 0402
C12: DNP; 0402
C13: 100p; 0402
C14: 1u; 0402
C19, C20: 6p; 0402
C23: 1.2p; 0402
C24: 0.8p; 0402
C25, C26: 12p; 0402
DEBUG1: CORTEX_DEBUGPTH; 2X5-PTH-1.27MM
IC2: NRF52832-EXTENDED; QFN48-6X6MM-EXTENDED
L2: 3.9nH; 0402
LED1, LED2: LED0805; CHIPLED_0805
R1, R2: 220; 0603
R6, R49, R60: 10k; 0402
U$18: BLE-ANT; ANT-2G4
UART: HEADER-1X5ROUND; 1X05_ROUND
UPDATE: 434111043826
Y1: 32MHz; CRYSTAL-SMD-2.0X1.6MM

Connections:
!RESET!: C22.1, DEBUG1.10 (!RESET), IC2.24 (P0.21/RESET), R60.2
ANT: C24.1, IC2.30 (ANT), L2.2
DCC: IC2.47 (DCC)
DEC4: C14.2, IC2.46 (DEC4)
DEC5: C11.2, IC2.1 (DEC1)
DEC6: C12.2, IC2.32 (DEC2)
DEC8: C13.2, IC2.33 (DEC3)
GND: C8.2, C9.2, C10.2, C11.1, C12.1, C13.1, C14.1, C19.1, C20.1, C21.2, C22.2, C23.2, C24.2, C25.2, C26.2, DEBUG1.3 (GND), DEBUG1.5 (GND), DEBUG1.9 (GNDDTCT), IC2.31 (VSS), IC2.45 (VSS), IC2.EP (VSS), LED1.C, LED2.C, R49.1, U$18.2, UART.1, UPDATE.1; also elsewhere on the board
I2C_SCL: IC2.39 (P0.27); also elsewhere on the board
I2C_SDA: C25.1, IC2.38 (P0.26); also elsewhere on the board
MIFA: C23.1, L2.1, U$18.1
MISO: IC2.41 (P0.29/AIN5)
MOSI: IC2.42 (P0.30/AIN6)
unnamed: LED2.A, R2.1
unnamed: LED1.A, R1.1
unnamed: C26.1, IC2.37 (P0.25)
P00: IC2.2 (P0.00/XL1)
P01: IC2.3 (P0.01/XL2)
P02: IC2.4 (P0.02/AIN0); also elsewhere on the board
P03: IC2.5 (P0.03/AIN1); also elsewhere on the board
P04: IC2.6 (P0.04/AIN2); also elsewhere on the board
P05: IC2.7 (P0.05/AIN3), UART.4
P06: IC2.8 (P0.06), UART.3
P07: IC2.9 (P0.07), UART.5
P08: IC2.10 (P0.08), UART.2
P09: IC2.11 (P0.09/NFC1)
P10: IC2.12 (P0.10/NFC2)
P11: IC2.14 (P0.11); also elsewhere on the board
P12: IC2.15 (P0.12); also elsewhere on the board
P13: IC2.16 (P0.13); also elsewhere on the board
P14: IC2.17 (P0.14); also elsewhere on the board
P15: IC2.18 (P0.15), R1.2
P16: C21.1, IC2.19 (P0.16), R6.1, UPDATE.2
P17: IC2.20 (P0.17); also elsewhere on the board
P19: IC2.22 (P0.19); also elsewhere on the board
P20: IC2.23 (P0.20), R2.2
P22: IC2.27 (P0.22)
P23: IC2.28 (P0.23)
P24: IC2.29 (P0.24)
P28: IC2.40 (P0.28/AIN4)
SCK: IC2.43 (P0.31/AIN7)
SWDCLK: DEBUG1.4 (SWDCLK/TCK), IC2.25 (SWDCLK), R49.2
SWDIO: DEBUG1.2 (SWDIO/TMS), IC2.26 (SWDIO)
SWO/TDO: DEBUG1.6 (SWO/TDO), IC2.21 (P0.18)
VDD_BLE: C8.1, C9.1, C10.1, DEBUG1.1 (VCC), IC2.13 (VDD), IC2.36 (VDD), IC2.48 (VDD), R6.2, R60.1; also elsewhere on the board
XC1: C20.2, IC2.34 (XC1(32MHZ)), Y1.3 (2)
XC2: C19.2, IC2.35 (XC2(32MHZ)), Y1.1

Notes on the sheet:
BT Module
Jarne Van Mulders
DRAMCO
NRF52832 (BLE INTERFACE)
Pin 13
Pin 36
Pin 48
nRF52832
Supply Decoupling
Cortex Debug Connector
nRF52832 Supply Range !1.7 - 3.6V DC!
Add DC/DC converter as power supply for nRF52 nRF will automatically switch between DC/DC and LDO to ensure minimal power consumption
add pull-down to swd-clk to prevent entering debug mode
NRF52832 RXI
NRF52832 TXI
NRF52832 RTS
NRF52832 CTS
RTS
CTS
UART CONNECTION
Button
ADC
https://www.infineon.com/dgdl/Infineon-AN91445_Antenna_Design_and_RF_Layout_Guidelines-ApplicationNotes-v09_00-EN.pdf
https://infocenter.nordicsemi.com/index.jsp?topic=%2Fug_nrf52832_pdk%2FUG%2Fnrf52_PDK%2Fhw_debug_out.html
Footprint updated (14/08/23)
LED 1
LED 2

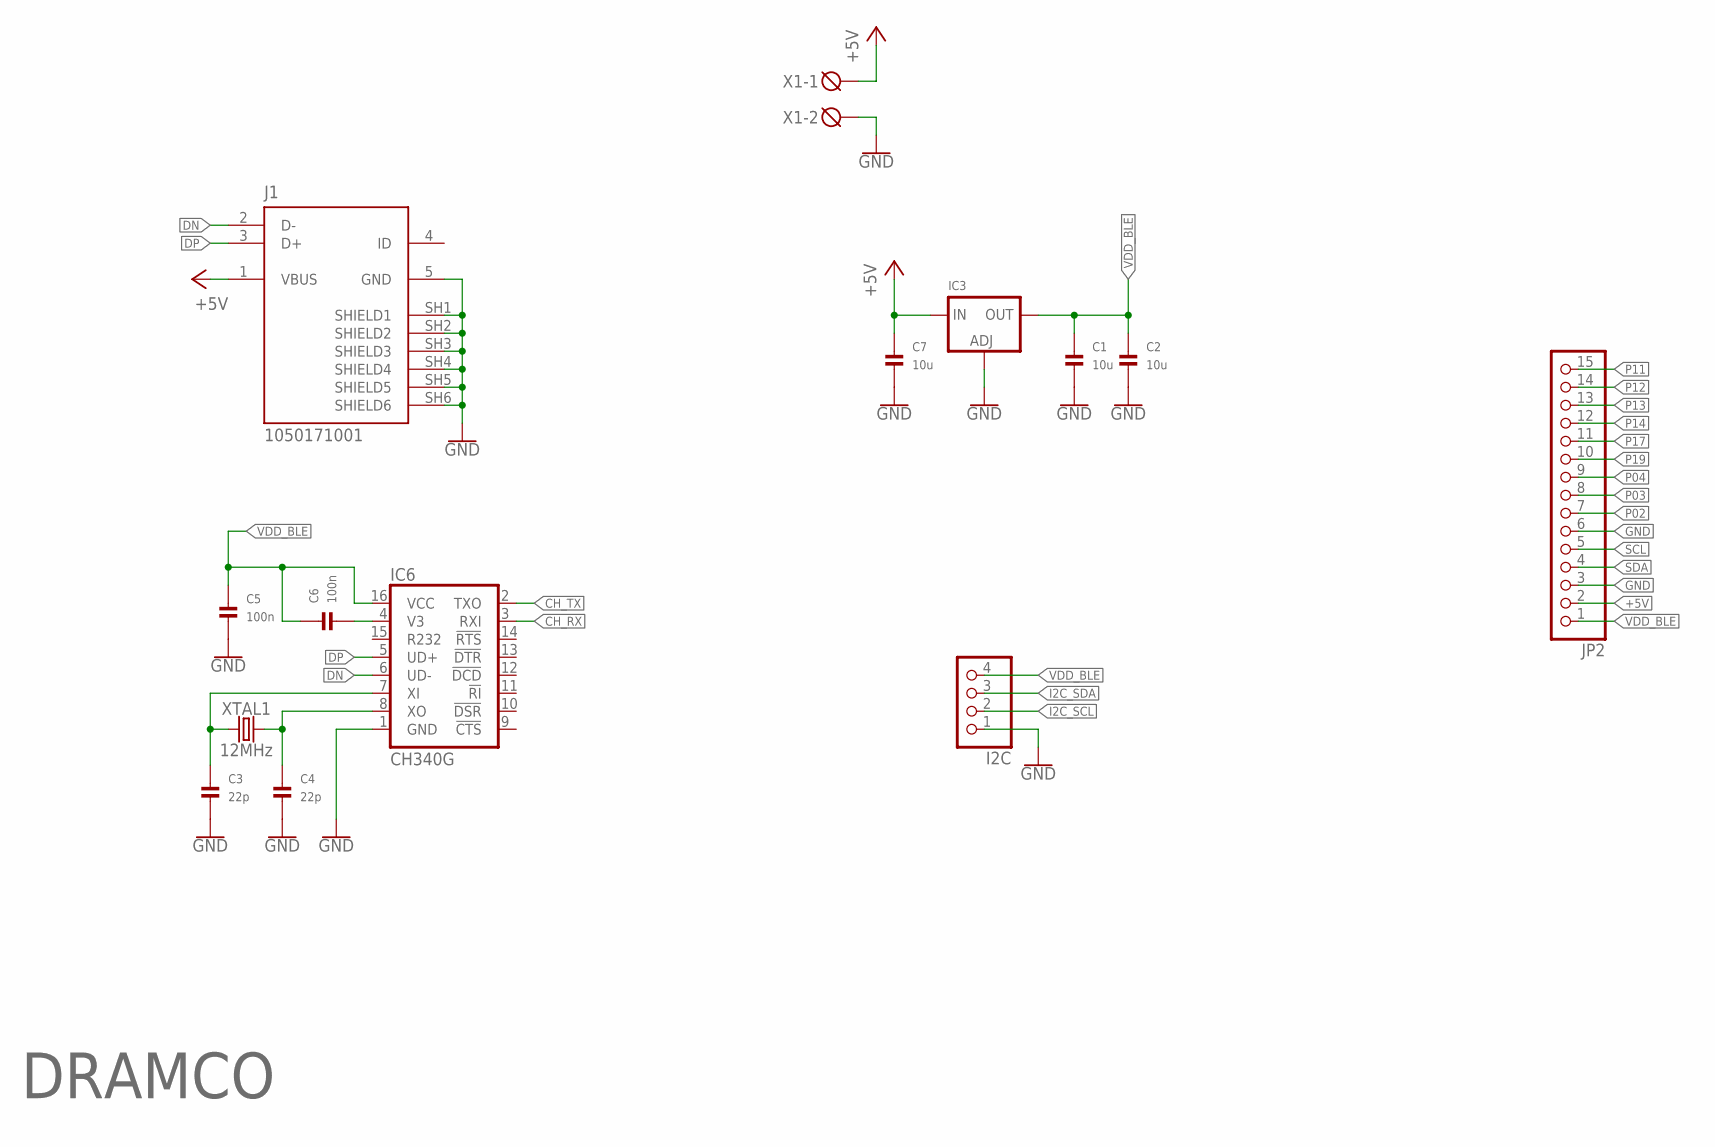
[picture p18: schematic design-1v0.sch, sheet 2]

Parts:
C1, C2, C7: 10u; 0805
C3, C4: 22p; 0402
C5, C6: 100n; 0402
I2C: HEADER-1X4ROUND; 1X04_ROUND
IC3: LM1117SOT223-REFLOW; SOT223-R
IC6: CH340G; SO016
J1: 1050171001; MOLEX_1050171001
JP2: HEADER-1X15; 1X15_ROUND_70
X1: DG3XX-02-3.5; DG350-3.5-02P
XTAL1: 12MHz; CRYSTAL-SMD-3.2X2.5MM

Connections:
+5V: C7.1, IC3.3 (IN), J1.1 (VBUS), JP2.2, X1.1
CH_RX: IC6.3 (RXI)
CH_TX: IC6.2 (TXO)
DN: IC6.6 (UD-), J1.2 (D-)
DP: IC6.5 (UD+), J1.3 (D+)
GND: C1.2, C2.2, C3.2, C4.2, C5.2, C7.2, I2C.1, IC3.1 (ADJ), IC6.1 (GND), J1.5 (GND), J1.SH1 (SHIELD1), J1.SH2 (SHIELD2), J1.SH3 (SHIELD3), J1.SH4 (SHIELD4), J1.SH5 (SHIELD5), J1.SH6 (SHIELD6), JP2.3, JP2.6, X1.2; also elsewhere on the board
I2C_SCL: I2C.2; also elsewhere on the board
I2C_SDA: I2C.3; also elsewhere on the board
unnamed: C3.1, IC6.7 (XI), XTAL1.1
unnamed: C4.1, IC6.8 (XO), XTAL1.3 (2)
unnamed: C6.2, IC6.4 (V3)
P02: JP2.7; also elsewhere on the board
P03: JP2.8; also elsewhere on the board
P04: JP2.9; also elsewhere on the board
P11: JP2.15; also elsewhere on the board
P12: JP2.14; also elsewhere on the board
P13: JP2.13; also elsewhere on the board
P14: JP2.12; also elsewhere on the board
P17: JP2.11; also elsewhere on the board
P19: JP2.10; also elsewhere on the board
SCL: JP2.5
SDA: JP2.4
VDD_BLE: C1.1, C2.1, C5.1, C6.1, I2C.4, IC3.2 (OUT), IC6.16 (VCC), JP2.1; also elsewhere on the board

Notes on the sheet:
DRAMCO

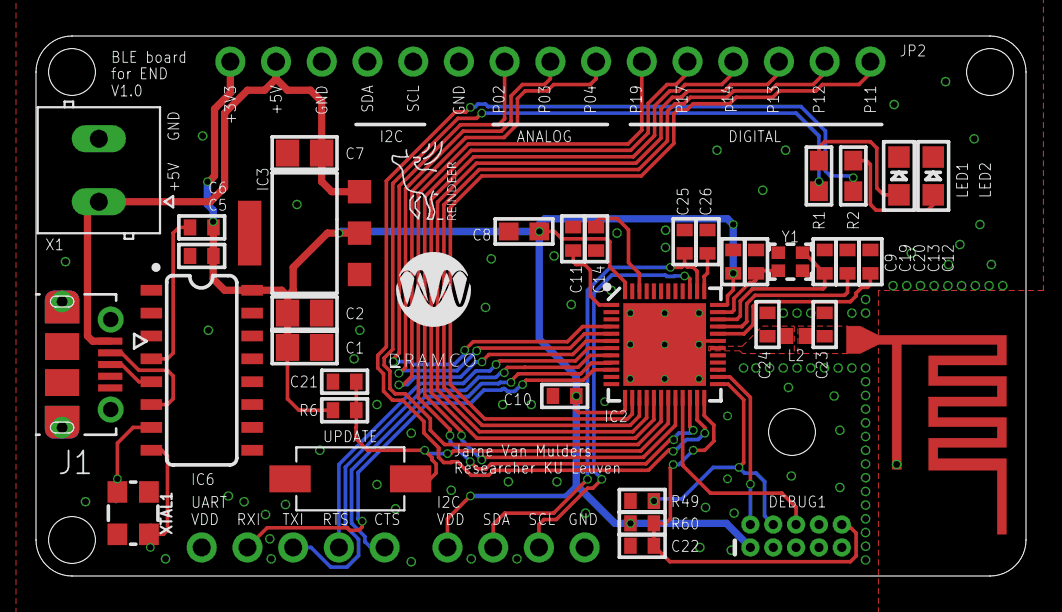
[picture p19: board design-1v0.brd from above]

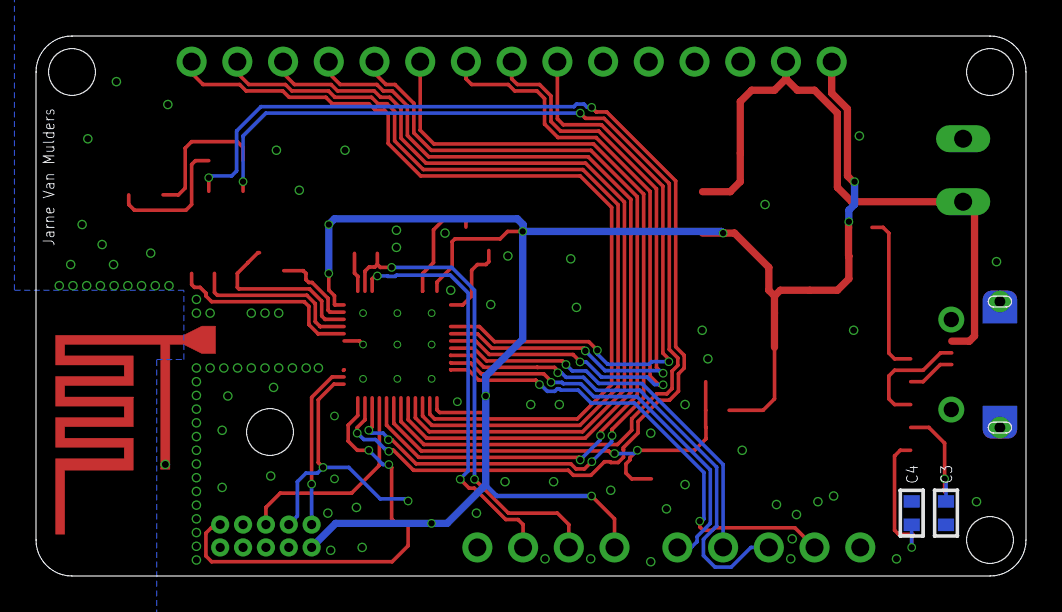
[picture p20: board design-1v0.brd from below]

Board: 2 copper layers, 55.0 x 30.0 mm, 43 parts (2 on the bottom side), 41 nets.

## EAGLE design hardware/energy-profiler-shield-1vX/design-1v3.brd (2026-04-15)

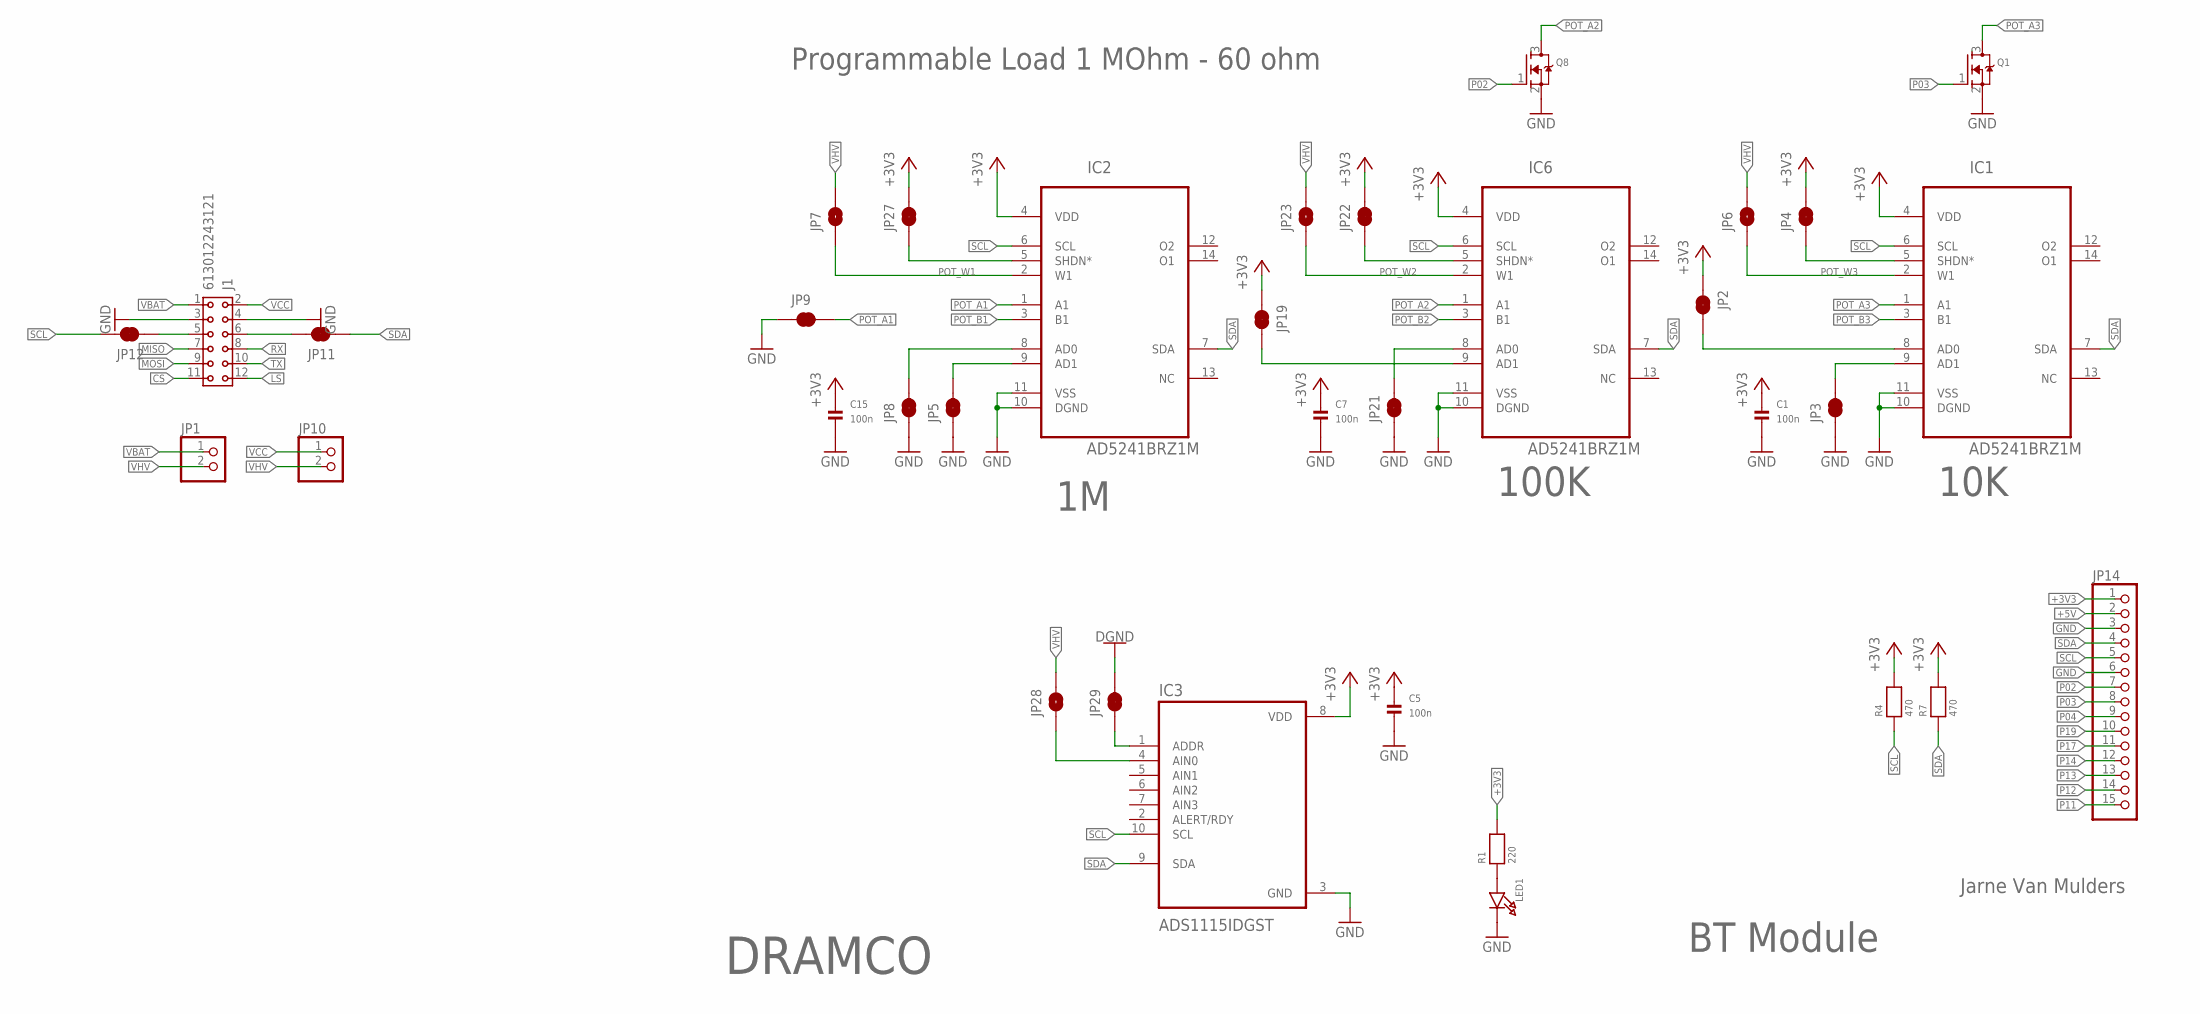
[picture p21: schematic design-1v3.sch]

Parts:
C1, C5, C7, C15: 100n; 0603
IC1, IC2, IC6: AD5241BRZ1M; SOIC127P600X175-14N
IC3: ADS1115IDGST; SOP50P490X110-10N
J1: 613012243121
JP1, JP10: HEADER-1X2ROUND; 1X02_ROUND
JP2, JP3, JP4, JP5, JP8, JP9, JP11, JP12, JP19, JP21, JP22, JP27, JP29: JUMPER-SMT_2_NC_TRACE_NO-SILK; SMT-JUMPER_2_NC_TRACE_NO-SILK
JP6, JP7, JP23, JP28: JUMPER-SMT_2_NO_NO-SILK; SMT-JUMPER_2_NO_NO-SILK
JP14: HEADER-1X15; 1X15_ROUND_70
LED1: LED0805; CHIPLED_0805
Q1, Q8: MOSFET-NREFLOW; SOT23-R
R1: 220; 0603
R4, R7: 470; 0603

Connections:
+3V3: C1.1, C5.1, C7.1, C15.1, IC1.4 (VDD), IC2.4 (VDD), IC3.8 (VDD), IC6.4 (VDD), JP2.1, JP4.2, JP14.1, JP19.1, JP22.2, JP27.2, R1.2, R4.2, R7.2
+5V: JP14.2
CS: J1.11
GND: C1.2, C5.2, C7.2, C15.2, IC1.10 (DGND), IC1.11 (VSS), IC2.10 (DGND), IC2.11 (VSS), IC3.3 (GND), IC6.10 (DGND), IC6.11 (VSS), J1.3, J1.4, JP3.1, JP5.1, JP8.1, JP9.1, JP14.3, JP14.6, JP21.1, JP29.2, LED1.C, Q1.2 (S), Q8.2 (S)
LS: J1.12
MISO: J1.7
MOSI: J1.9
unnamed: IC1.8 (AD0), JP2.2
unnamed: IC1.9 (AD1), JP3.2
unnamed: IC1.5 (SHDN*), JP4.1
unnamed: J1.5, JP12.1
unnamed: J1.6, JP11.2
unnamed: IC6.9 (AD1), JP19.2
unnamed: IC6.8 (AD0), JP21.2
unnamed: IC2.5 (SHDN*), JP27.1
unnamed: IC2.8 (AD0), JP8.2
unnamed: IC2.9 (AD1), JP5.2
unnamed: LED1.A, R1.1
unnamed: IC3.4 (AIN0), JP28.1
unnamed: IC3.1 (ADDR), JP29.1
unnamed: IC6.5 (SHDN*), JP22.1
P02: JP14.7, Q8.1 (G)
P03: JP14.8, Q1.1 (G)
P04: JP14.9
P11: JP14.15
P12: JP14.14
P13: JP14.13
P14: JP14.12
P17: JP14.11
P19: JP14.10
POT_A1: IC2.1 (A1), JP9.2
POT_A2: IC6.1 (A1), Q8.3 (D)
POT_A3: IC1.1 (A1), Q1.3 (D)
POT_B1: IC2.3 (B1)
POT_B2: IC6.3 (B1)
POT_B3: IC1.3 (B1)
POT_W1: IC2.2 (W1), JP7.1
POT_W2: IC6.2 (W1), JP23.1
POT_W3: IC1.2 (W1), JP6.1
RX: J1.8
SCL: IC1.6 (SCL), IC2.6 (SCL), IC3.10 (SCL), IC6.6 (SCL), JP12.2, JP14.5, R4.1
SDA: IC1.7 (SDA), IC2.7 (SDA), IC3.9 (SDA), IC6.7 (SDA), JP11.1, JP14.4, R7.1
TX: J1.10
VBAT: J1.1, JP1.1
VCC: J1.2, JP10.1
VHV: JP1.2, JP6.2, JP7.2, JP10.2, JP23.2, JP28.2

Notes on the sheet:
BT Module
Jarne Van Mulders
DRAMCO
100K
10K
Programmable Load 1 MOhm - 60 ohm

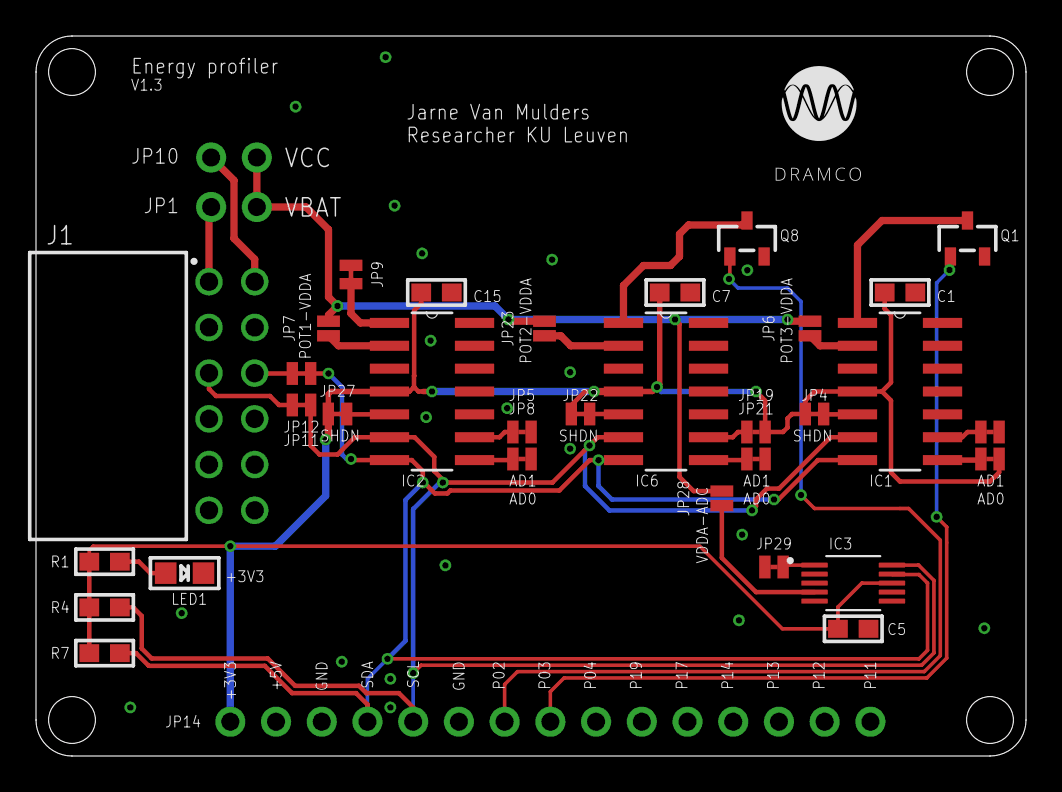
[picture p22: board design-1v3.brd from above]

Board: 2 copper layers, 55.0 x 40.0 mm, 35 parts (0 on the bottom side), 29 nets.

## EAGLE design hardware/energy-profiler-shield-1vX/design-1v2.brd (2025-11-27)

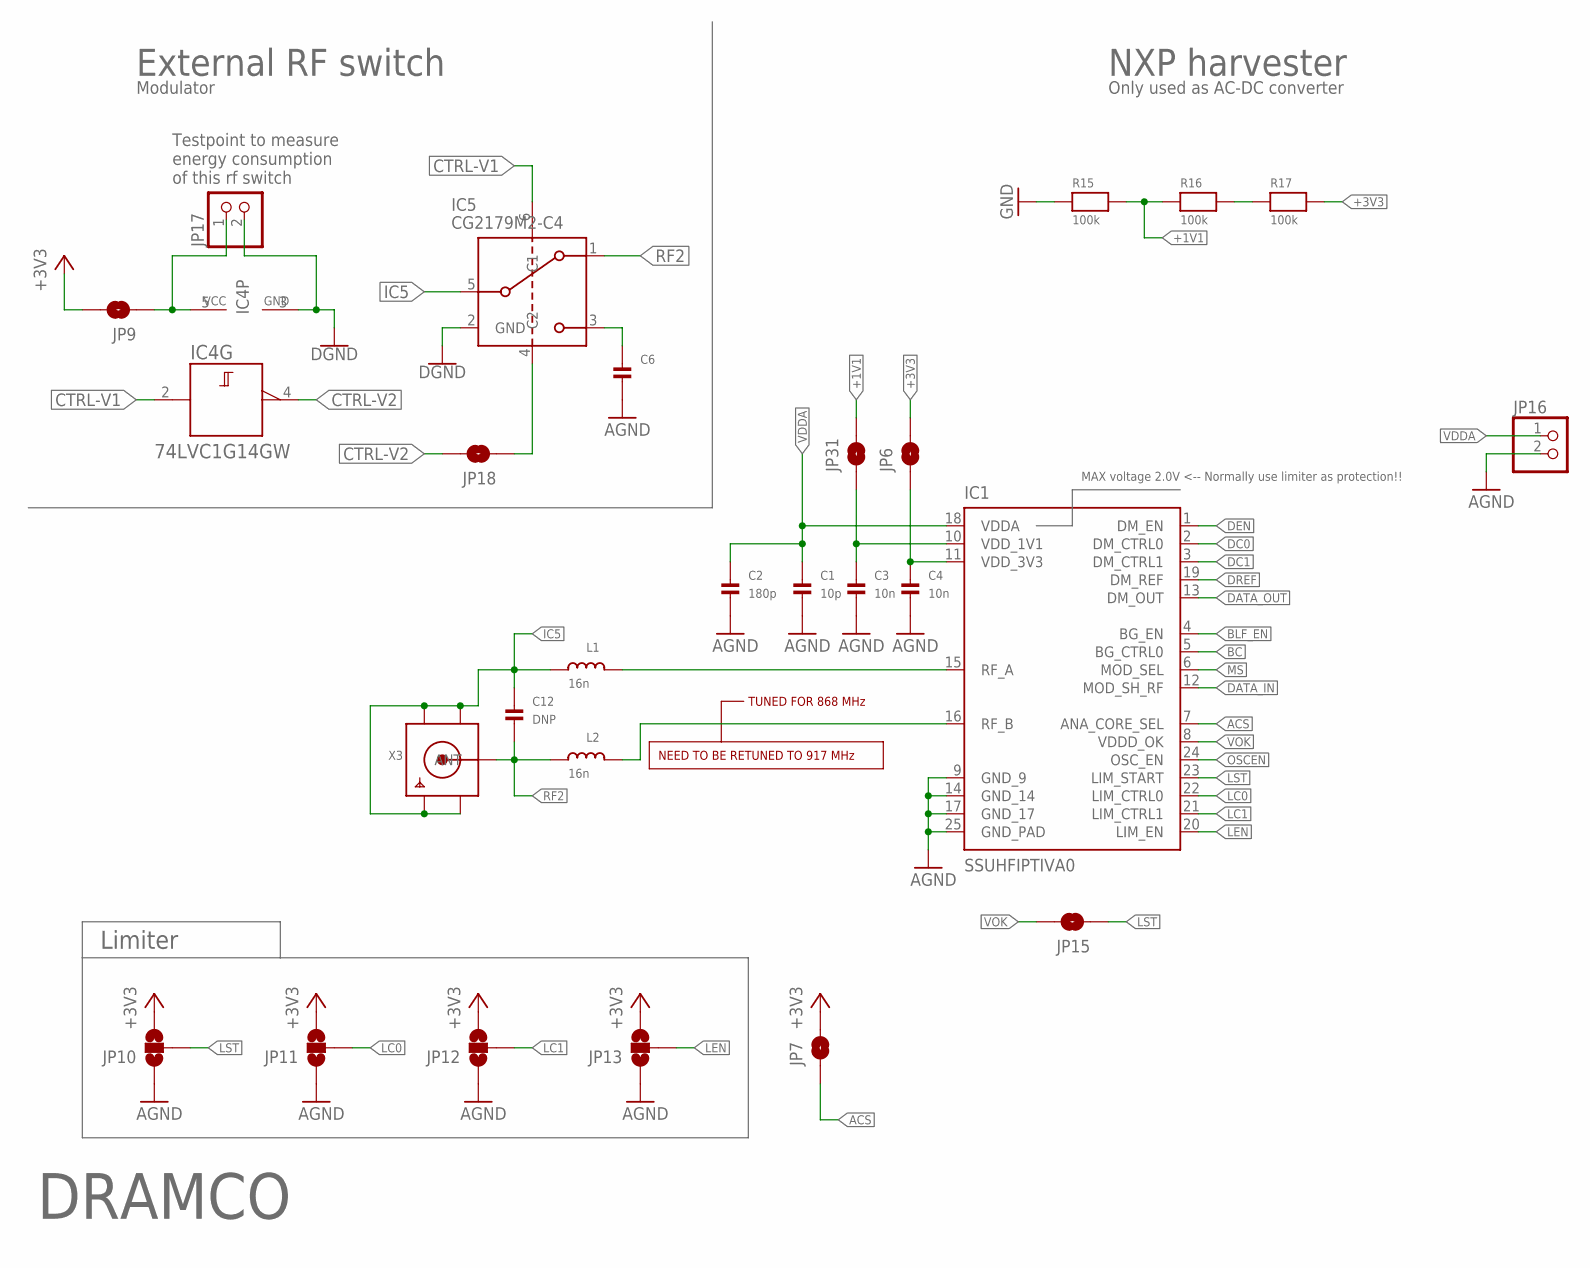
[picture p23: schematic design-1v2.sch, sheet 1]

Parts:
C1: 10p; 0603
C2: 180p; 0603
C3, C4: 10n; 0603
C6: CAP_CERAMIC0402; 0402
C12: DNP; 0402
IC1: SSUHFIPTIVA0; QFN50P400X400X90-25N
IC4: 74LVC1G14GW; SOT353-1
IC5: CG2179M2-C4; SC70-6-CNC04
JP6, JP7, JP9, JP15, JP18, JP31: JUMPER-SMT_2_NO_NO-SILK; SMT-JUMPER_2_NO_NO-SILK
JP10, JP11, JP12, JP13: JUMPER-SMT_3_NO_SILK; SMT-JUMPER_3_NO_SILK
JP16, JP17: HEADER-1X2ROUND; 1X02_ROUND
L1, L2: 16n; _0402
R15, R16, R17: 100k; 0603
X3: SMACONNECTOR_EDGE_UFL; SMA_EDGELAUNCH_UFL

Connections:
+1V1: JP31.2, R15.2, R16.1
+3V3: JP6.2, JP7.2, JP9.2, JP10.3, JP11.3, JP12.3, JP13.3, R17.2; also elsewhere on the board
ACS: IC1.7 (ANA_CORE_SEL), JP7.1
AGND: C1.2, C2.2, C3.2, C4.2, C6.2, IC1.9 (GND_9), IC1.14 (GND_14), IC1.17 (GND_17), IC1.25 (GND_PAD), JP10.1, JP11.1, JP12.1, JP13.1, JP16.2; also elsewhere on the board
BC: IC1.5 (BG_CTRL0)
BLF_EN: IC1.4 (BG_EN)
CTRL-V1: IC4.2 (A), IC5.6 (C1); also elsewhere on the board
CTRL-V2: IC4.4 (Y), JP18.2
DATA_IN: IC1.12 (MOD_SH_RF)
DATA_OUT: IC1.13 (DM_OUT)
DC0: IC1.2 (DM_CTRL0)
DC1: IC1.3 (DM_CTRL1)
DEN: IC1.1 (DM_EN)
DREF: IC1.19 (DM_REF)
GND: IC4.3 (GND), IC5.2 (GND), JP17.2, R15.1; also elsewhere on the board
IC5: C12.1, IC5.5 (PC), L1.1, X3.GND@1 (GND1), X3.GND@2 (GND2), X3.GND@3 (GND3), X3.GND@4 (GND4)
LC0: IC1.22 (LIM_CTRL0), JP11.2
LC1: IC1.21 (LIM_CTRL1), JP12.2
LEN: IC1.20 (LIM_EN), JP13.2
LST: IC1.23 (LIM_START), JP10.2, JP15.1
MS: IC1.6 (MOD_SEL)
unnamed: C4.1, IC1.11 (VDD_3V3), JP6.1
unnamed: C3.1, IC1.10 (VDD_1V1), JP31.1
unnamed: IC1.15 (RF_A), L1.2
unnamed: IC1.16 (RF_B), L2.2
unnamed: IC5.4 (C2), JP18.1
unnamed: C6.1, IC5.3 (P2)
unnamed: IC4.5 (VCC), JP9.1, JP17.1
unnamed: R16.2, R17.1
OSCEN: IC1.24 (OSC_EN)
RF2: C12.2, IC5.1, L2.1, X3.P (ANT)
VDDA: C1.1, C2.1, IC1.18 (VDDA), JP16.1; also elsewhere on the board
VOK: IC1.8 (VDDD_OK), JP15.2

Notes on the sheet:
Limiter
MAX voltage 2.0V <-- Normally use limiter as protection!!
TUNED FOR 868 MHz
NEED TO BE RETUNED TO 917 MHz
NXP harvester
Only used as AC-DC converter
DRAMCO
External RF switch
Modulator
Testpoint to measure energy consumption of this rf switch

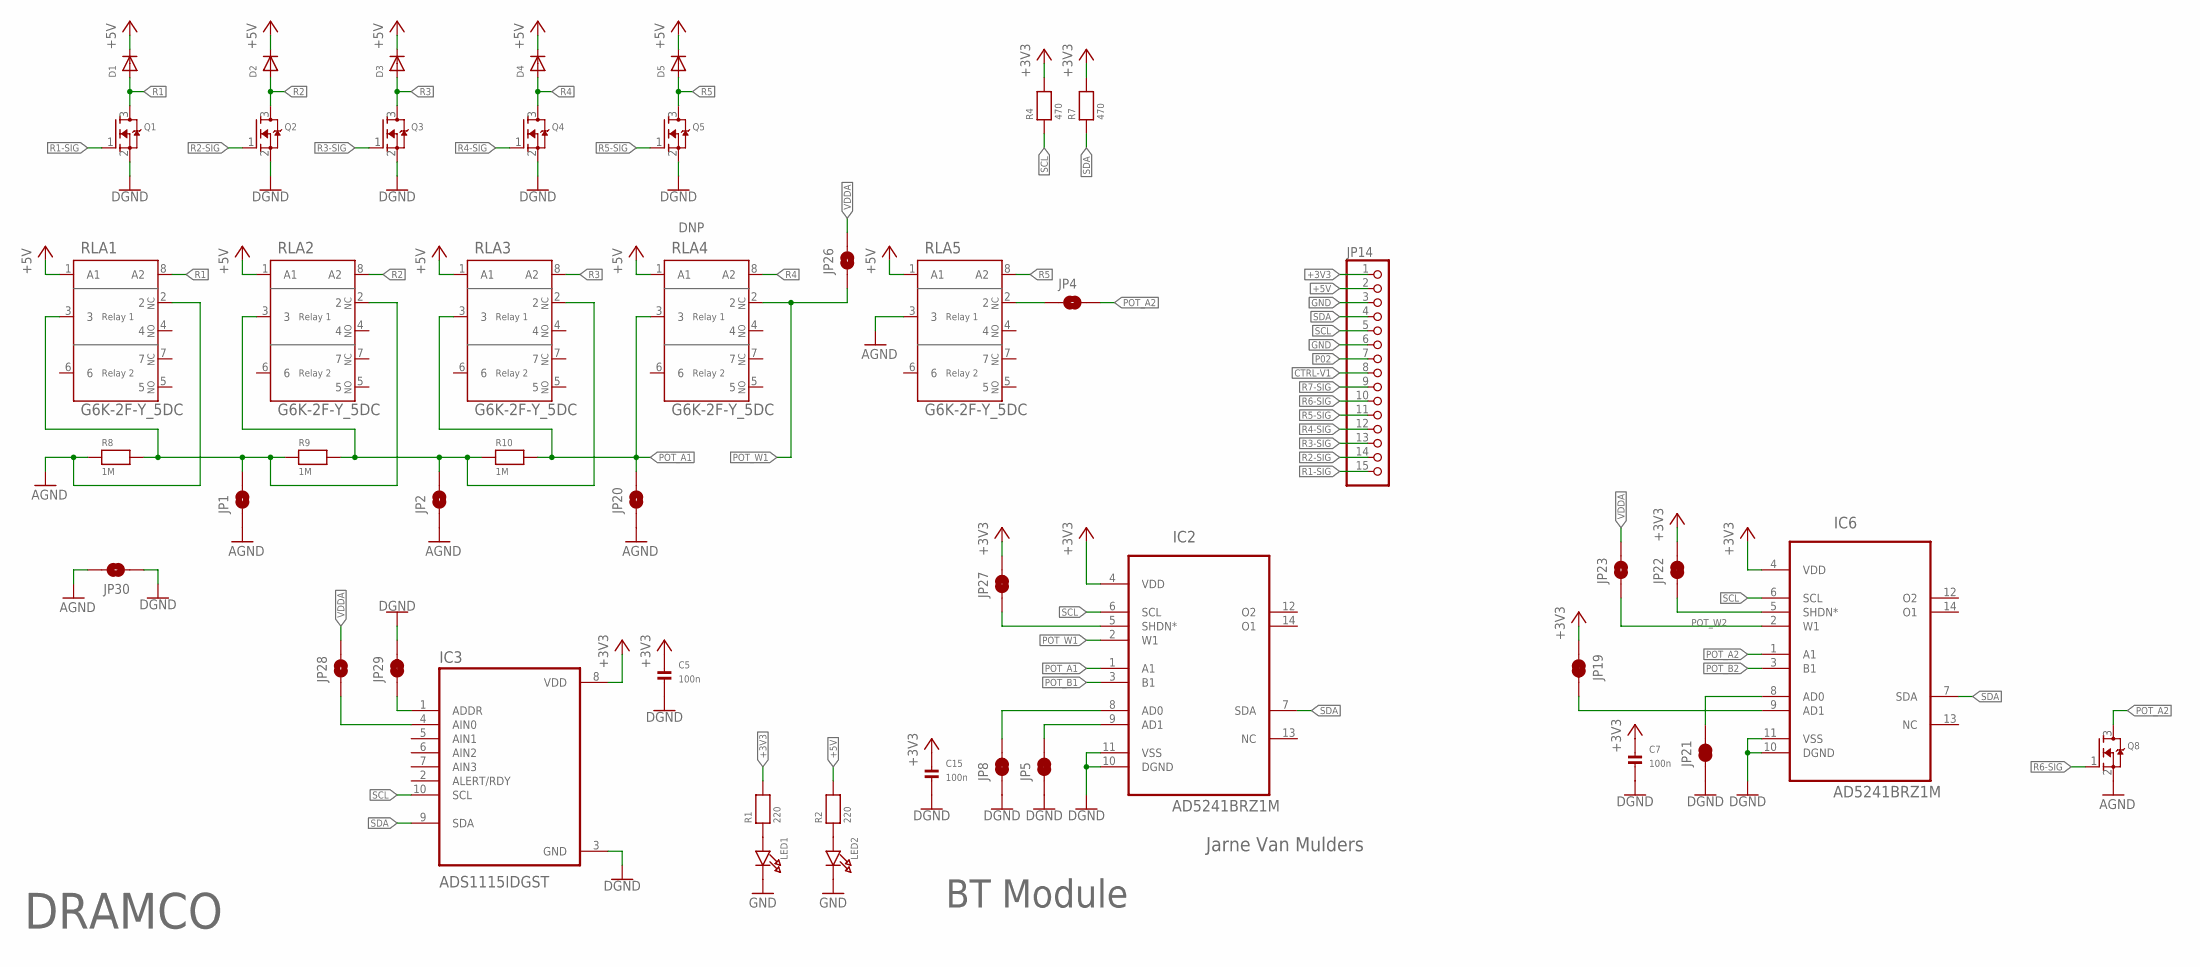
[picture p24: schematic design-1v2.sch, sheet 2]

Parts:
C5, C7, C15: 100n; 0603
D1, D2, D3, D4, D5: DIODESOD-123; SOD-123
IC2, IC6: AD5241BRZ1M; SOIC127P600X175-14N
IC3: ADS1115IDGST; SOP50P490X110-10N
JP1, JP2, JP4, JP20, JP23, JP26, JP28, JP30: JUMPER-SMT_2_NO_NO-SILK; SMT-JUMPER_2_NO_NO-SILK
JP5, JP8, JP19, JP21, JP22, JP27, JP29: JUMPER-SMT_2_NC_TRACE_NO-SILK; SMT-JUMPER_2_NC_TRACE_NO-SILK
JP14: HEADER-1X15; 1X15_ROUND_70
LED1, LED2: LED0805; CHIPLED_0805
Q1, Q2, Q3, Q4, Q5, Q8: MOSFET-NREFLOW; SOT23-R
R1, R2: 220; 0603
R4, R7: 470; 0603
R8, R9, R10: 1M; 0805
RLA1, RLA2, RLA3, RLA4, RLA5: G6K-2F-Y_5DC; RELAY_G6K-2F_OMR

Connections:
+3V3: C5.1, C7.1, C15.1, IC2.4 (VDD), IC3.8 (VDD), IC6.4 (VDD), JP14.1, JP19.1, JP22.2, JP27.2, R1.2, R4.2, R7.2; also elsewhere on the board
+5V: D1.C, D2.C, D3.C, D4.C, D5.C, JP14.2, R2.2, RLA1.1 (A1), RLA2.1 (A1), RLA3.1 (A1), RLA4.1 (A1), RLA5.1 (A1)
AGND: JP1.1, JP2.1, JP20.1, JP30.2, Q8.2 (S), R8.1, RLA1.2, RLA5.3; also elsewhere on the board
CTRL-V1: JP14.8; also elsewhere on the board
GND: C5.2, C7.2, C15.2, IC2.10 (DGND), IC2.11 (VSS), IC3.3 (GND), IC6.10 (DGND), IC6.11 (VSS), JP5.1, JP8.1, JP14.3, JP14.6, JP21.1, JP29.2, JP30.1, LED1.C, LED2.C, Q1.2 (S), Q2.2 (S), Q3.2 (S), Q4.2 (S), Q5.2 (S); also elsewhere on the board
unnamed: LED2.A, R2.1
unnamed: JP2.2, R9.2, R10.1, RLA2.3, RLA3.2
unnamed: IC6.9 (AD1), JP19.2
unnamed: JP1.2, R8.2, R9.1, RLA1.3, RLA2.2
unnamed: IC6.8 (AD0), JP21.2
unnamed: JP4.1, RLA5.2
unnamed: IC2.5 (SHDN*), JP27.1
unnamed: IC2.8 (AD0), JP8.2
unnamed: IC2.9 (AD1), JP5.2
unnamed: LED1.A, R1.1
unnamed: IC3.4 (AIN0), JP28.1
unnamed: IC3.1 (ADDR), JP29.1
unnamed: IC6.5 (SHDN*), JP22.1
P02: JP14.7
POT_A1: IC2.1 (A1), JP20.2, R10.2, RLA3.3, RLA4.3
POT_A2: IC6.1 (A1), JP4.2, Q8.3 (D)
POT_B1: IC2.3 (B1)
POT_B2: IC6.3 (B1)
POT_W1: IC2.2 (W1), JP26.1, RLA4.2
POT_W2: IC6.2 (W1), JP23.1
R1: D1.A, Q1.3 (D), RLA1.8 (A2)
R1-SIG: JP14.15, Q1.1 (G)
R2: D2.A, Q2.3 (D), RLA2.8 (A2)
R2-SIG: JP14.14, Q2.1 (G)
R3: D3.A, Q3.3 (D), RLA3.8 (A2)
R3-SIG: JP14.13, Q3.1 (G)
R4: D4.A, Q4.3 (D), RLA4.8 (A2)
R4-SIG: JP14.12, Q4.1 (G)
R5: D5.A, Q5.3 (D), RLA5.8 (A2)
R5-SIG: JP14.11, Q5.1 (G)
R6-SIG: JP14.10, Q8.1 (G)
R7-SIG: JP14.9
SCL: IC2.6 (SCL), IC3.10 (SCL), IC6.6 (SCL), JP14.5, R4.1
SDA: IC2.7 (SDA), IC3.9 (SDA), IC6.7 (SDA), JP14.4, R7.1
VDDA: JP23.2, JP26.2, JP28.2; also elsewhere on the board

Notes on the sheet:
BT Module
Jarne Van Mulders
DRAMCO
DNP

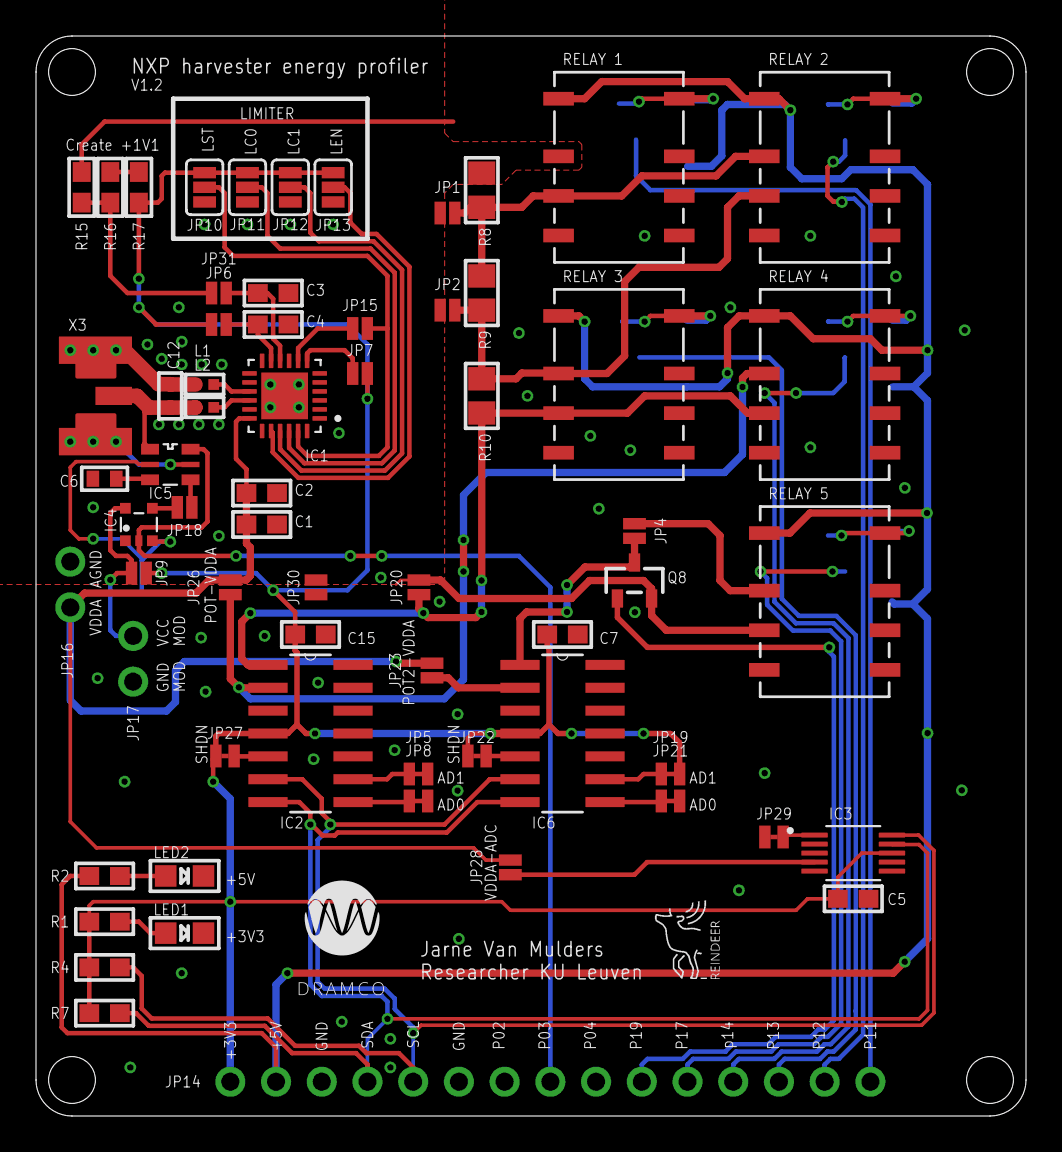
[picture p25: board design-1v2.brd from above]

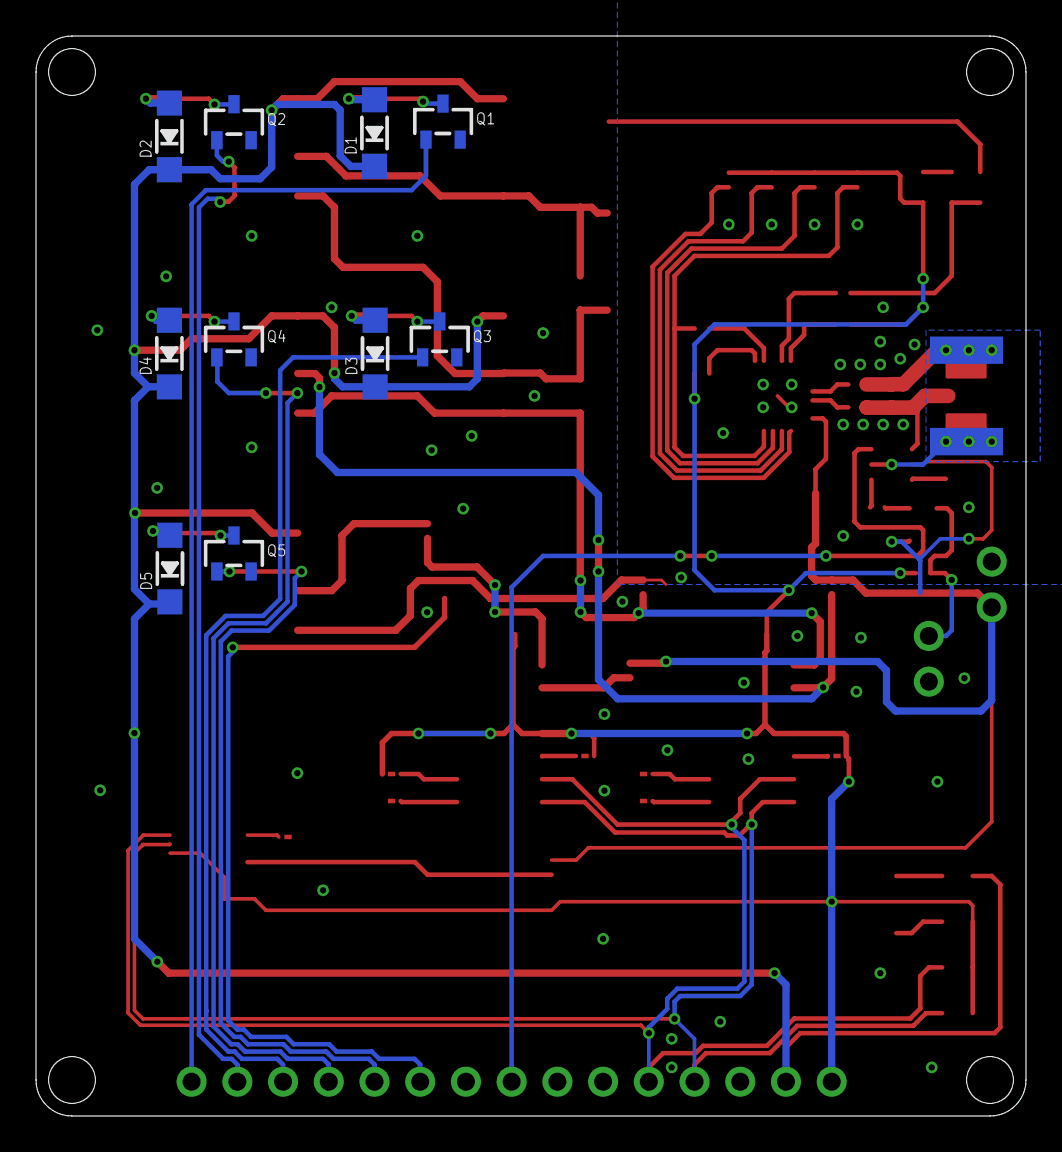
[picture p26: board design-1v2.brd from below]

Board: 2 copper layers, 55.0 x 60.0 mm, 74 parts (10 on the bottom side), 54 nets.

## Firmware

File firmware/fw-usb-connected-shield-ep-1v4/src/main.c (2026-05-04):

/*  ____  ____      _    __  __  ____ ___
 * |  _ \|  _ \    / \  |  \/  |/ ___/ _ \
 * | | | | |_) |  / _ \ | |\/| | |  | | | |
 * | |_| |  _ <  / ___ \| |  | | |__| |_| |
 * |____/|_| \_\/_/   \_\_|  |_|\____\___/
 *                           research group
 *                             dramco.be/
 *
 *  KU Leuven - Technology Campus Gent,
 *  Gebroeders De Smetstraat 1,
 *  B-9000 Gent, Belgium
 *
 *         File: main.c
 *      Created: 2024-03-20
 *       Author: Jarne Van Mulders
 *      Version: major.minor
 *
 *  Description: END BLE monitor board
 * 
 *  Commissiond by Reindeer POC and demonstrator
 */

#include <inttypes.h>
#include <stddef.h>
#include <stdint.h>
#include "stdio.h"
#include <zephyr/kernel.h>
#include <zephyr/devicetree.h>
#include <zephyr/drivers/uart.h>

//  Include lookup table header
#include "lookup_table/lookup_table.h"

//  Include settings
#include "init.h"

//  Include external I2C peripherals
#include "peripherals/peripherals.h"

//  Timer settings LED blink
uint16_t delay_on_ms = 500;
uint16_t delay_off_ms = 500;
struct k_timer my_timer;

//  Potentiometer settings
int32_t pot_val = 0;
#define LOWER_BOUNDARY 0 
#define UPPER_BOUNDARY 719//487 // Lowest resistance
uint32_t target_voltage = SETPOINT;

//  Variables for UART
int32_t buffer_voltage_mv;
uint32_t resistance;
uint32_t pwr_pw;

//  GPIO pins
struct gpio_dt_spec blue_led_pin = GPIO_DT_SPEC_GET(DT_ALIAS(usrled0), gpios);
struct gpio_dt_spec red_led_pin = GPIO_DT_SPEC_GET(DT_ALIAS(usrled1), gpios);
struct gpio_dt_spec pot100k_pin = GPIO_DT_SPEC_GET(DT_ALIAS(pot100k), gpios);
struct gpio_dt_spec pot10k_pin = GPIO_DT_SPEC_GET(DT_ALIAS(pot10k), gpios);

//  UART device
const struct device *uart = DEVICE_DT_GET(DT_NODELABEL(uart0));

//  Static functions
static uint8_t calculate_xor_checksum(const uint8_t* buffer, size_t length);
static bool parse_frame(const uint8_t *buf, size_t len, uint8_t *cmd, uint32_t *value);
static int debugger();
static uint8_t rx_buf[1000] = { 0 };

//  Stack size and debug priority
#define STACKSIZE 1024
#define DBG_PRIORITY 8

//  *** START THREADS *** //
K_THREAD_DEFINE(debugger_id, STACKSIZE, debugger, NULL, NULL, NULL, DBG_PRIORITY, 0, 0);

//  P controller gains
#define KP 0.02     // Proportional gain

//  Upper and lower setpoint limits
uint32_t upper_set_point = 0;
uint32_t lower_set_point = 0;

//  Other global variables
uint32_t num = 0;
uint32_t max_voltage = 0;
uint8_t timer_elapsed = 0;

// Define uint8_t transmit array to store converted values
uint8_t buf8 [19]; // 1 (start) + 1 (length) + 4*4 (data) + 1 (checksum)
uint32_t buf32 [4]; 

// //  Lookup table for resistance values corresponding to potentiometer settings
// const float lookup_table[719] = { 959538.00f, 956019.00f, 952684.00f, 949355.00f, 946061.00f, 942132.00f, 938460.00f, 935074.00f, 931683.00f, 928149.00f, 924660.00f, 921208.00f, 917833.00f, 914309.00f, 910815.00f, 907424.00f, 904003.00f, 900504.00f, 897026.00f, 893558.00f, 889978.00f, 886664.00f, 883196.00f, 879488.00f, 876056.00f, 872537.00f, 868997.00f, 865422.00f, 861888.00f, 858446.00f, 855009.00f, 851495.00f, 847935.00f, 844334.00f, 840774.00f, 837322.00f, 833834.00f, 830294.00f, 826719.00f, 823102.00f, 819553.00f, 816044.00f, 812566.00f, 809022.00f, 805328.00f, 801661.00f, 798229.00f, 794900.00f, 791611.00f, 788205.00f, 784763.00f, 781008.00f, 776967.00f, 773289.00f, 769775.00f, 766277.00f, 762758.00f, 759080.00f, 755433.00f, 751847.00f, 748277.00f, 744712.00f, 741178.00f, 737521.00f, 733910.00f, 730303.00f, 726764.00f, 723204.00f, 719583.00f, 715982.00f, 712350.00f, 708898.00f, 705138.00f, 701522.00f, 697875.00f, 694253.00f, 690576.00f, 686934.00f, 683379.00f, 679839.00f, 676085.00f, 672310.00f, 668765.00f, 665205.00f, 661569.00f, 657896.00f, 654249.00f, 650628.00f, 646945.00f, 643318.00f, 639661.00f, 635998.00f, 632351.00f, 628694.00f, 625022.00f, 621380.00f, 617666.00f, 613983.00f, 610249.00f, 606633.00f, 603037.00f, 599272.00f, 595297.00f, 591615.00f, 588065.00f, 584582.00f, 580996.00f, 577190.00f, 573431.00f, 569779.00f, 566142.00f, 562418.00f, 558669.00f, 554965.00f, 551282.00f, 547543.00f, 543870.00f, 540162.00f, 536479.00f, 532740.00f, 528975.00f, 525190.00f, 521548.00f, 517757.00f, 514054.00f, 510351.00f, 506555.00f, 502877.00f, 499066.00f, 495297.00f, 491603.00f, 487869.00f, 484084.00f, 480401.00f, 476805.00f, 473076.00f, 468953.00f, 465198.00f, 461516.00f, 457694.00f, 453904.00f, 450144.00f, 446400.00f, 442620.00f, 438829.00f, 435105.00f, 431269.00f, 427525.00f, 423765.00f, 419980.00f, 416169.00f, 412378.00f, 408542.00f, 404762.00f, 400956.00f, 397047.00f, 393365.00f, 389656.00f, 385779.00f, 381937.00f, 378085.00f, 374233.00f, 370427.00f, 366606.00f, 362805.00f, 358984.00f, 355153.00f, 351337.00f, 347470.00f, 343654.00f, 339797.00f, 335781.00f, 332006.00f, 328220.00f, 324368.00f, 320547.00f, 316670.00f, 312833.00f, 308961.00f, 305124.00f, 301242.00f, 297390.00f, 293599.00f, 289645.00f, 285773.00f, 281885.00f, 278002.00f, 274104.00f, 270232.00f, 266380.00f, 262426.00f, 258610.00f, 254614.00f, 250737.00f, 246828.00f, 242936.00f, 239043.00f, 235160.00f, 231206.00f, 227282.00f, 223374.00f, 219455.00f, 215501.00f, 211629.00f, 207710.00f, 203802.00f, 199889.00f, 195944.00f, 191995.00f, 188056.00f, 184117.00f, 180194.00f, 176234.00f, 172295.00f, 168320.00f, 164381.00f, 160422.00f, 156478.00f, 152503.00f, 148554.00f, 144605.00f, 140655.00f, 136675.00f, 132716.00f, 128598.00f, 124623.00f, 120648.00f, 116668.00f, 112688.00f, 108698.00f, 104697.00f, 100712.00f, 87181.50f, 86873.80f, 86565.50f, 86257.80f, 85950.60f, 85643.30f, 85335.10f, 85026.80f, 84716.50f, 84406.10f, 84096.80f, 83787.50f, 83478.20f, 83168.30f, 82859.00f, 82546.50f, 82207.80f, 81898.50f, 81588.70f, 81280.40f, 80970.60f, 80660.70f, 80348.80f, 80033.70f, 79717.00f, 79401.90f, 79089.00f, 78776.00f, 78464.00f, 78150.00f, 77835.40f, 77520.90f, 77171.10f, 76857.10f, 76542.00f, 76226.90f, 75912.80f, 75596.70f, 75281.10f, 74965.00f, 74648.80f, 74333.20f, 74015.50f, 73697.20f, 73381.10f, 73062.30f, 72746.20f, 72426.90f, 72095.50f, 71776.20f, 71457.50f, 71137.10f, 70818.90f, 70499.60f, 70180.80f, 69860.50f, 69541.70f, 69218.80f, 68896.80f, 68577.00f, 68256.70f, 67935.80f, 67613.90f, 67291.50f, 66951.20f, 66628.20f, 66305.20f, 65982.80f, 65659.30f, 65336.30f, 65012.80f, 64689.30f, 64365.30f, 64040.30f, 63716.80f, 63389.60f, 63066.10f, 62740.50f, 62414.90f, 62089.30f, 61748.50f, 61420.80f, 61091.50f, 60763.80f, 60437.70f, 60111.60f, 59787.60f, 59459.90f, 59130.60f, 58801.40f, 58472.60f, 58144.40f, 57815.10f, 57484.80f, 57156.10f, 56825.70f, 56477.00f, 56147.30f, 55816.90f, 55485.00f, 55154.20f, 54822.30f, 54490.90f, 54159.00f, 53826.60f, 53494.70f, 53161.80f, 52827.80f, 52495.90f, 52161.90f, 51828.40f, 51494.40f, 51151.50f, 50817.00f, 50482.50f, 50146.90f, 49812.40f, 49475.70f, 49141.80f, 48807.80f, 48472.70f, 48131.40f, 47793.20f, 47457.10f, 47120.40f, 46781.70f, 46444.10f, 46105.90f, 45750.30f, 45412.10f, 45073.40f, 44733.60f, 44394.90f, 44053.60f, 43715.90f, 43375.10f, 43034.80f, 42693.40f, 42353.10f, 42011.30f, 41669.90f, 41328.00f, 40985.60f, 40641.70f, 40292.40f, 39950.60f, 39607.10f, 39262.10f, 38919.70f, 38575.70f, 38231.80f, 37887.30f, 37542.80f, 37197.70f, 36852.70f, 36506.60f, 36161.60f, 35814.00f, 35467.90f, 35121.80f, 34758.40f, 34410.80f, 34063.60f, 33716.00f, 33368.30f, 33019.60f, 32672.00f, 32322.80f, 31974.10f, 31623.80f, 31275.10f, 30924.30f, 30575.10f, 30225.30f, 29873.50f, 29521.60f, 29162.90f, 28812.10f, 28460.30f, 28107.40f, 27754.50f, 27402.10f, 27049.70f, 26696.30f, 26343.90f, 25988.90f, 25635.00f, 25280.50f, 24926.00f, 24570.50f, 24216.00f, 23859.50f, 23483.40f, 23126.90f, 22770.30f, 22413.20f, 22056.10f, 21699.50f, 21342.40f, 20984.30f, 20627.20f, 20268.00f, 19908.80f, 19550.10f, 19190.90f, 18831.10f, 18471.90f, 18111.20f, 17743.60f, 17382.80f, 17021.50f, 16659.60f, 16297.80f, 15936.50f, 15574.70f, 15212.30f, 14850.00f, 14486.60f, 14123.20f, 13759.80f, 13395.80f, 13031.40f, 12667.50f, 12301.40f, 11924.90f, 11559.90f, 11193.90f, 10828.40f, 10462.40f, 10094.70f, 9728.70f, 9361.60f, 9670.40f, 9635.20f, 9599.00f, 9562.20f, 9527.10f, 9489.30f, 9454.10f, 9416.80f, 9381.10f, 9344.80f, 9308.60f, 9271.80f, 9236.10f, 9163.90f, 9128.29f, 9091.41f, 9041.42f, 9005.60f, 8969.77f, 8933.06f, 8897.44f, 8860.57f, 8824.85f, 8788.13f, 8752.46f, 8715.54f, 8679.87f, 8643.20f, 8607.64f, 8570.71f, 8535.15f, 8498.22f, 8445.98f, 8410.05f, 8374.22f, 8337.45f, 8301.79f, 8264.86f, 8229.14f, 8192.32f, 8156.65f, 8119.72f, 8084.05f, 8047.29f, 8011.62f, 7974.74f, 7938.86f, 7902.04f, 7851.90f, 7815.97f, 7780.09f, 7743.22f, 7707.39f, 7670.52f, 7634.74f, 7598.03f, 7562.20f, 7525.17f, 7489.55f, 7452.57f, 7416.96f, 7379.98f, 7344.21f, 7307.33f, 7254.98f, 7219.00f, 7183.02f, 7146.20f, 7110.37f, 7073.44f, 7037.62f, 7000.69f, 6964.97f, 6927.94f, 6892.06f, 6855.19f, 6819.47f, 6782.54f, 6746.66f, 6709.79f, 6659.43f, 6623.35f, 6587.42f, 6550.59f, 6514.66f, 6477.63f, 6441.75f, 6404.93f, 6368.95f, 6331.97f, 6296.09f, 6259.22f, 6223.39f, 6186.41f, 6150.54f, 6113.50f, 6061.05f, 6024.91f, 5988.98f, 5952.05f, 5916.07f, 5879.04f, 5843.11f, 5806.18f, 5770.25f, 5733.22f, 5697.29f, 5660.26f, 5624.48f, 5587.45f, 5551.47f, 5514.49f, 5463.98f, 5427.79f, 5391.80f, 5354.77f, 5318.79f, 5281.70f, 5245.72f, 5208.74f, 5172.76f, 5135.68f, 5099.75f, 5062.71f, 5026.84f, 4989.70f, 4953.72f, 4916.69f, 4864.28f, 4828.09f, 4791.95f, 4754.92f, 4718.88f, 4681.70f, 4645.77f, 4608.68f, 4572.70f, 4535.61f, 4499.58f, 4462.49f, 4426.46f, 4389.38f, 4353.39f, 4316.31f, 4265.80f, 4229.55f, 4193.36f, 4156.33f, 4120.19f, 4083.05f, 4047.02f, 4009.88f, 3973.79f, 3936.65f, 3900.62f, 3863.48f, 3827.50f, 3790.42f, 3754.28f, 3717.14f, 3664.42f, 3628.18f, 3591.99f, 3554.85f, 3518.71f, 3481.52f, 3445.38f, 3408.30f, 3372.16f, 3334.97f, 3298.88f, 3261.69f, 3225.66f, 3188.47f, 3152.27f, 3115.19f, 3064.31f, 3028.07f, 2991.77f, 2954.58f, 2918.39f, 2881.14f, 2844.95f, 2807.82f, 2771.62f, 2734.38f, 2698.29f, 2661.05f, 2624.96f, 2587.72f, 2551.53f, 2514.29f, 2461.57f, 2425.28f, 2389.03f, 2351.74f, 2315.54f, 2278.25f, 2242.06f, 2204.82f, 2168.62f, 2131.33f, 2095.14f, 2057.84f, 2021.70f, 1984.41f, 1948.16f, 1910.98f, 1860.10f, 1823.69f, 1787.40f, 1750.10f, 1713.80f, 1676.51f, 1640.27f, 1602.97f, 1566.73f, 1529.28f, 1493.14f, 1455.74f, 1419.65f, 1382.25f, 1346.06f, 1308.66f, 1255.84f, 1219.38f, 1182.98f, 1145.63f, 1109.34f, 1071.99f, 1035.64f, 998.29f, 962.05f, 924.65f, 893.94f, 856.16f, 819.60f, 781.80f, 745.14f, 707.43f, 653.43f, 616.65f, 579.94f, 542.31f, 505.69f, 468.02f, 431.45f, 393.85f, 357.30f, 319.63f, 283.14f, 245.54f, 209.12f, 171.48f, 134.96f };

// Timer callback function
void my_timer_handler(struct k_timer *dummy) {
    timer_elapsed = 1;
}

bool new_uart_message = false;

const uint8_t *buf;
size_t len;

//  UART callback function
static void uart_cb(const struct device* dev, struct uart_event* evt, void* user_data)
{
	switch (evt->type) {

    case UART_RX_RDY:
        //  Get pointer to received data and its length
        buf = evt->data.rx.buf + evt->data.rx.offset;
        len = evt->data.rx.len;

        new_uart_message = true;

        break;

	default:
		break;
	}
}
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

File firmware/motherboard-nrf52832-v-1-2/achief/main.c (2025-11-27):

/*  ____  ____      _    __  __  ____ ___
 * |  _ \|  _ \    / \  |  \/  |/ ___/ _ \
 * | | | | |_) |  / _ \ | |\/| | |  | | | |
 * | |_| |  _ <  / ___ \| |  | | |__| |_| |
 * |____/|_| \_\/_/   \_\_|  |_|\____\___/
 *                           research group
 *                             dramco.be/
 *
 *  KU Leuven - Technology Campus Gent,
 *  Gebroeders De Smetstraat 1,
 *  B-9000 Gent, Belgium
 *
 *         File: main.c
 *      Created: 2024-03-20
 *       Author: Jarne Van Mulders
 *      Version: major.minor
 *
 *  Description: END BLE monitor board
 * 
 *  Commissiond by Reindeer POC and demonstrator
 */

#include <inttypes.h>
#include <stddef.h>
#include <stdint.h>
#include "stdio.h"

#include <zephyr/kernel.h>
#include <zephyr/devicetree.h>
#include <zephyr/drivers/gpio.h>

//  Include external I2C peripherals
#include "peripherals/peripherals.h"

#include "advertisement/advertisement.h"

#include "nrf.h"

uint16_t delay_on_ms = 500;
uint16_t delay_off_ms = 500;

// uint8_t pot_val = 255; // for safety start with lowest resistance
uint16_t pot_val;
#define LOWER_BOUNDARY 0 
#define UPPER_BOUNDARY 255//487//255 // Lowest resistance

int32_t buffer_voltage_mv;
uint32_t resistance;
uint32_t pwr_nw;

// uint8_t counter = 0;

//  GPIO pins
struct gpio_dt_spec blue_led_pin = GPIO_DT_SPEC_GET(DT_ALIAS(usrled0), gpios);
struct gpio_dt_spec red_led_pin = GPIO_DT_SPEC_GET(DT_ALIAS(usrled1), gpios);
struct gpio_dt_spec relay1_pin = GPIO_DT_SPEC_GET(DT_ALIAS(relay1), gpios);
struct gpio_dt_spec relay2_pin = GPIO_DT_SPEC_GET(DT_ALIAS(relay2), gpios);
struct gpio_dt_spec relay3_pin = GPIO_DT_SPEC_GET(DT_ALIAS(relay3), gpios);
struct gpio_dt_spec relay4_pin = GPIO_DT_SPEC_GET(DT_ALIAS(relay4), gpios);
struct gpio_dt_spec relay5_pin = GPIO_DT_SPEC_GET(DT_ALIAS(relay5), gpios);
struct gpio_dt_spec relay6_pin = GPIO_DT_SPEC_GET(DT_ALIAS(relay6), gpios);
struct gpio_dt_spec relay7_pin = GPIO_DT_SPEC_GET(DT_ALIAS(relay7), gpios);

/* size of stack area used by each thread */
#define STACKSIZE 1024

/* scheduling priority used by each thread */
#define ADV_PRIORITY 7
#define DBG_PRIORITY 8

static void debugger();

// *** START THREADS *** //
K_THREAD_DEFINE(start_adv_id, STACKSIZE, adv_start, NULL, NULL, NULL, ADV_PRIORITY, 0, 0);
K_THREAD_DEFINE(debugger_id, STACKSIZE, debugger, NULL, NULL, NULL, DBG_PRIORITY, 0, 0);

#define KP 0.01     // Proportional gain
// #define KI 0.1      // Integral gain
// #define KD 0        // Derivative gain

#define SETPOINT    1600    //  mV
#define SP_ACCURAY  50      //  mV

uint32_t upper_set_point = SETPOINT + SP_ACCURAY;
uint32_t lower_set_point = SETPOINT - SP_ACCURAY;

// Other global variables
uint32_t num = 0;
uint32_t max_voltage = 0;

#define LOOP
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

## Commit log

2025-11-27 Remove length print statement
    Removed debug print statement for length.
2025-12-12 Fix print statement to show power consumption
2026-01-19 Update hardware folder
    [design-1v0.brd, design-1v0.sch, design-1v1.brd, design-1v1.sch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]
2026-03-04 Add validation results
    [1768988429_ADS-disconnected_results.csv, 1768989903_ADS-connected_results.csv, 1769002865_ADS-connected_results.csv, 1769003043_ADS-connected_results.csv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]
2026-03-04 Add images and sections to README for calibration
2026-03-04 Update README with calibration details
    Added details about the HAMEG HM8112-3 connection and calibration process for the energy profiler.
2026-03-04 add 02 js measurements
    [1771605183_measurements.csv, 1772613019_measurements.csv, 1772613084_measurements.csv, 1772614526_measurements.csv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]
2026-03-04 Revise README for JouleScope power sweep results
    Updated section titles and added explanations for power calculations in the JouleScope measurements.
2026-03-05 Add 03
    [1772702121_measurements.csv]
2026-03-05 Update README with voltage measurement details
    Added explanation for voltage measurement with JouleScope.
2026-04-15 Add hw 1v3
    [design-1.GBL, design-1.GBO, design-1.GBP, design-1.GBS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]

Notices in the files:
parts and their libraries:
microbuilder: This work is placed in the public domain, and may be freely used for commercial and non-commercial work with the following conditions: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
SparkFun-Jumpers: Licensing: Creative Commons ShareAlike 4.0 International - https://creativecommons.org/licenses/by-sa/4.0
